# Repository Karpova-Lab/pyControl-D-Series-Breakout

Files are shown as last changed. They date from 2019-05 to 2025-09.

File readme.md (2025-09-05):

- View documentation at  https://karpova-lab.github.io/pyControl-D-Series-Breakout/
- Ask questions at https://github.com/Karpova-Lab/pyControl-D-series-Breakout/discussions
- Clone repository from https://github.com/Karpova-Lab/pyControl-D-Series-Breakout

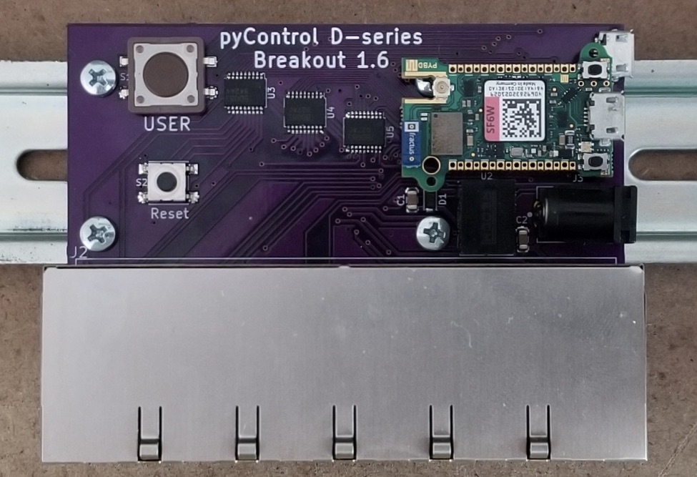
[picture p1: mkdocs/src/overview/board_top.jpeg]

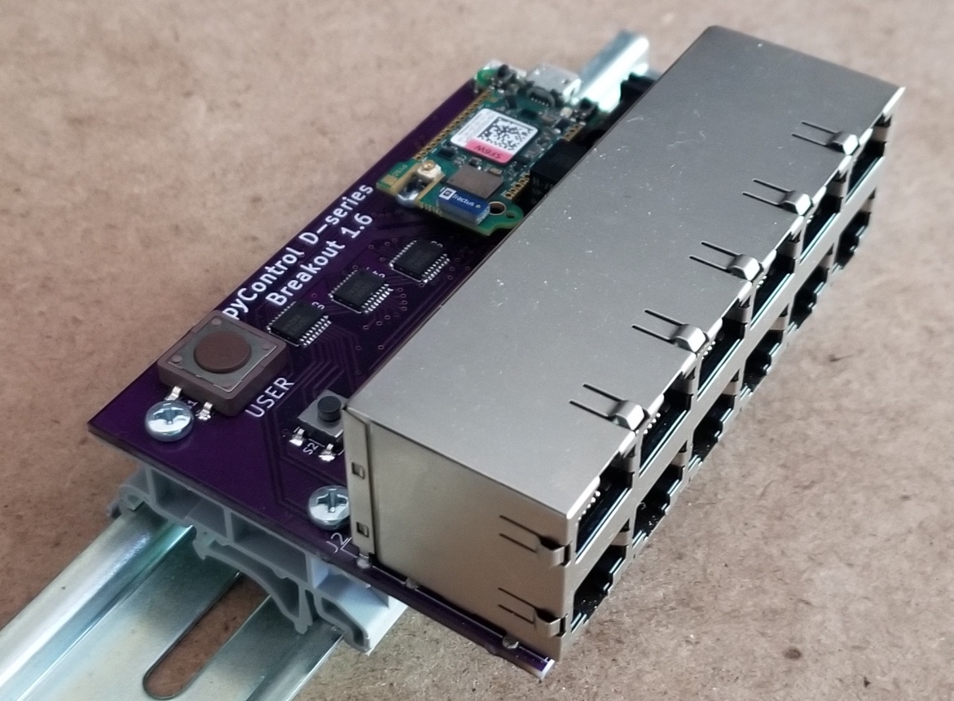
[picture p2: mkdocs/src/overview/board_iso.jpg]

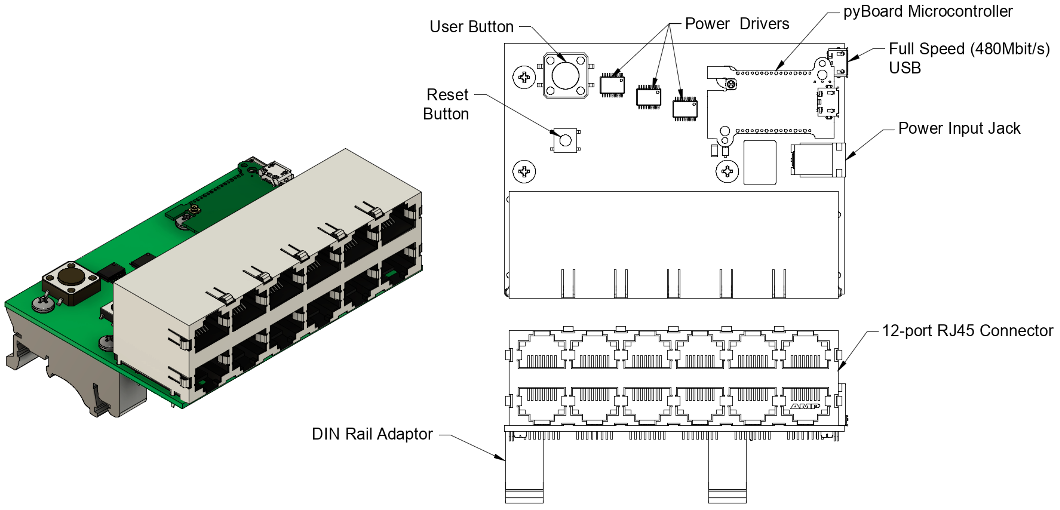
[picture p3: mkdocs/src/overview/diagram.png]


## License
This project is licensed under the [Janelia open-source hardware license](license_hardare.txt) and [Janelia 3-term BSD open-source software license](license_software.txt).

Please contact [innovation@janelia.hhmi.org](mailto:innovation@janelia.hhmi.org) if you have any questions about licensing or would like to use this project commercially.

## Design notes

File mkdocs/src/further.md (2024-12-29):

# Further Resources

## pyControl 

- [Official pyControl documentation](https://pycontrol.readthedocs.io/en/latest/) 
- [pyControl forum](https://github.com/orgs/pyControl/discussions) 
- [pyControl on GitHub](https://github.com/pyControl) 
- Purchase ready to use pyControl hardware at the [Open Ephys Store](http://www.open-ephys.org/pycontrol) or [Labmaker](https://www.labmaker.org/collections/neuroscience/products/pycontrol-mouse-behaviour-box_set_no1)

<a href="open_ephys.png">
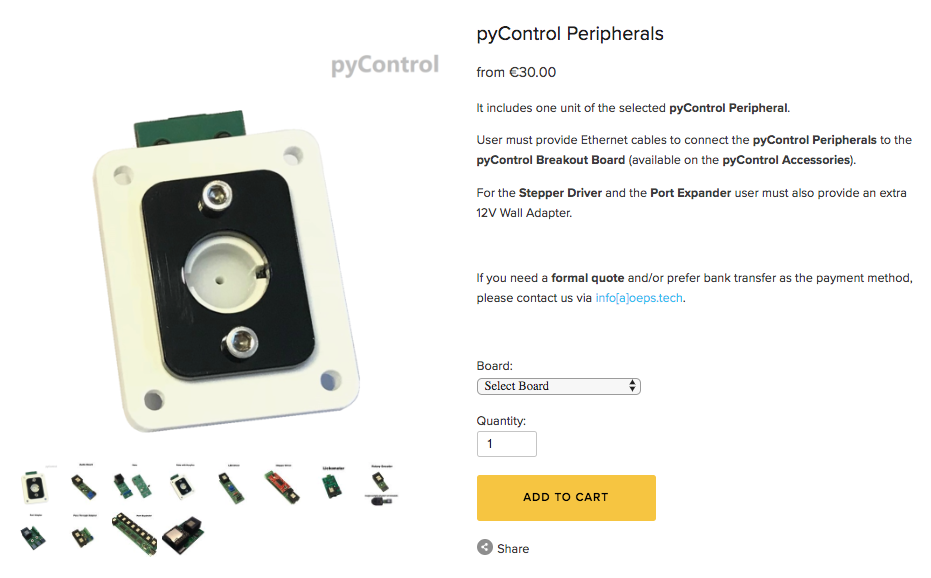
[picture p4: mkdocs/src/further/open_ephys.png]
    
</a>

## MicroPython and Pyboard D-series

- [MicroPython Documentation](http://docs.micropython.org/en/latest/) 
- [MicroPython Store](https://store.micropython.org/) 
- [Pyboard D-series Documentation](https://pybd.io/hw/pybd_sfxw.html) 

<a href="dseries.jpg">
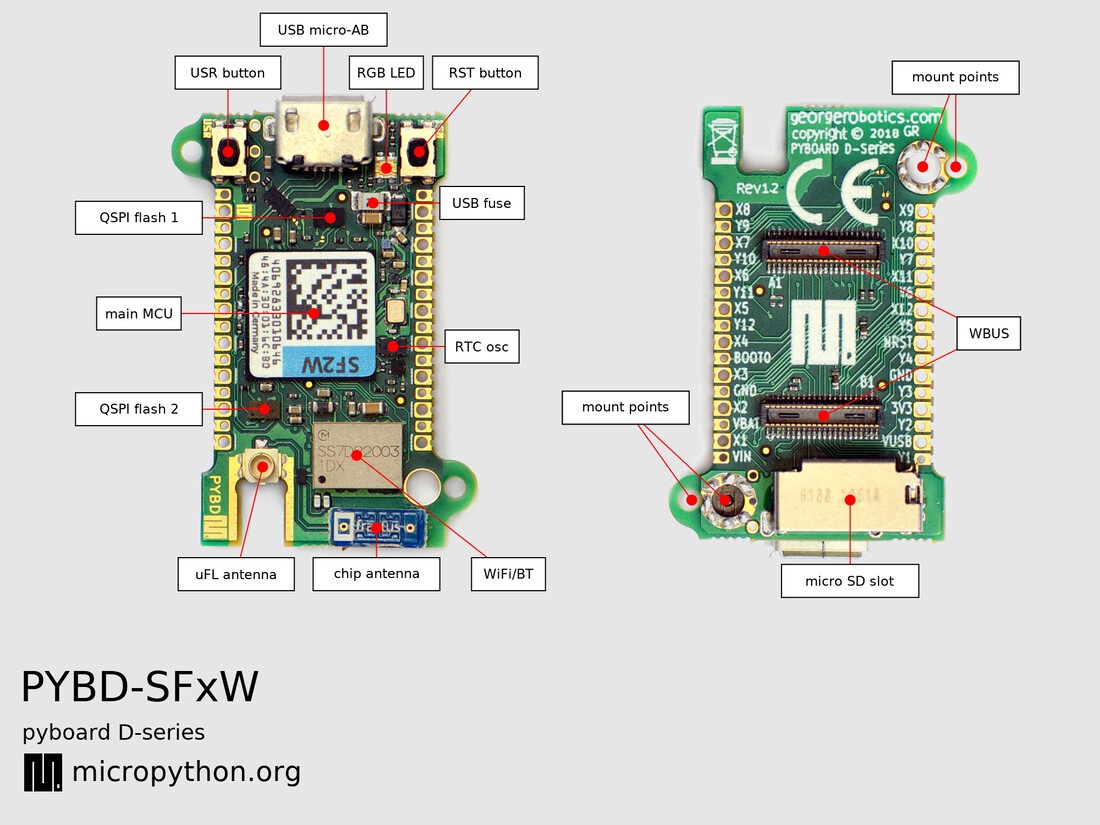
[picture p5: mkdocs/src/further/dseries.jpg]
    
</a>

## Karpova Lab
- [Lab website](https://www.janelia.org/lab/karpova-lab)
- [D-series breakout repository](https://github.com/Karpova-Lab/pyControl-D-series-Breakout)
- [More open hardware repositories](https://github.com/Karpova-Lab?type=source)
    - [Cerebro](https://karpova-lab.github.io/cerebro/)
    - [Lever](https://karpova-lab.github.io/lever/)
    - [Syringe Pump](https://karpova-lab.github.io/syringe-pump/)
    - [Nosepoke](https://karpova-lab.github.io/nosepoke/)

<a href="board_top.jpeg">
    
</a>

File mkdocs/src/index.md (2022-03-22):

# Overview

<a href="overview/board_iso.jpg">
  
</a>
<a href="overview/board_top.jpeg">
  
</a>
<a href="overview/diagram.png">
  
</a>

## What is this?

pyControl D-series breakout is a device that connects a [pyboard D-series microcontroller](https://pybd.io/hw/pybd_sfxw.html)  with twelve RJ45 ports. 
It is intended for use with the [pyControl](https://pycontrol.readthedocs.io/en/latest/) behavioral experiment control framework.

## How is it different?

<figure markdown>
  <a href="overview/side_by_side.jpeg">
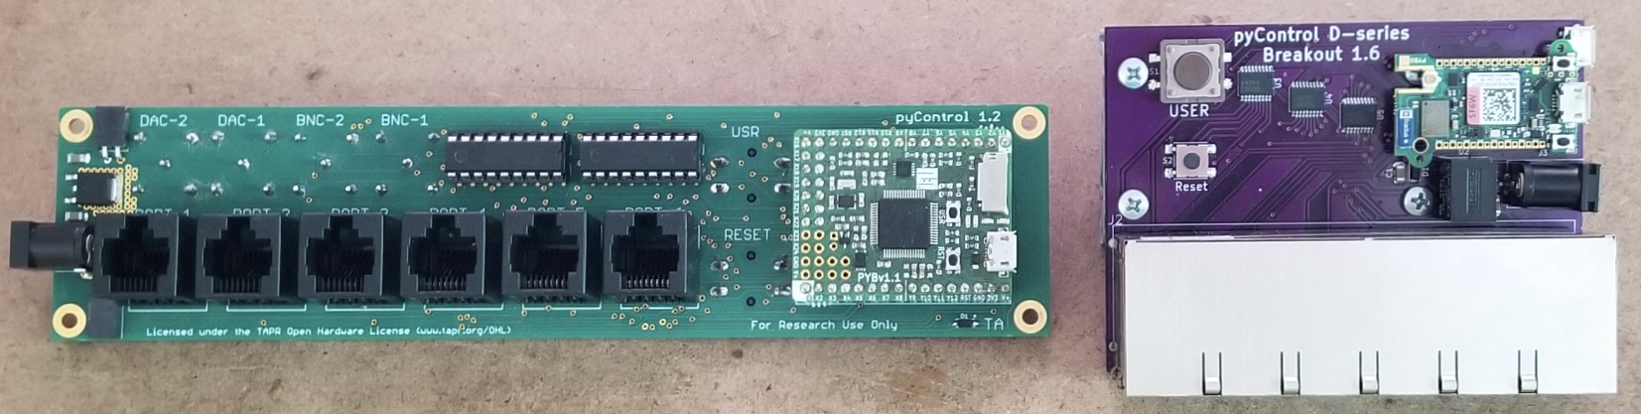
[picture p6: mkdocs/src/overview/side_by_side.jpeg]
    
  </a>
  <figcaption>pyControl Breakout Board 1.2 (left) and D-series Breakout (right)</figcaption>
</figure>

The core distinction between this breakout board and the official [pyControl breakout board 1.2](https://pycontrol.readthedocs.io/en/latest/user-guide/hardware/#breakout-board-12) is the upgrade to a newer generation pyboard (i.e. a more powerful microcontroller). 
Some benefits of the newer pyboard include being smaller, faster, having more memory, and having more input/output pins.
Having more available pins is particularly useful, as it enables the breakout board to provide more behavior ports without requiring a [port expander](https://pycontrol.readthedocs.io/en/latest/user-guide/hardware/#port-expander). 
Below is a comparison of the two breakout boards.

|                        | Breakout Board 1.2                                                | D-series Breakout Board 1.6                                                    |
|------------------------|-------------------------------------------------------------------|--------------------------------------------------------------------------------|
| **Microcontroller**    |                                                                   |                                                                                |
|    *Board*             | [pyboard v1.1](https://store.micropython.org/product/PYBv1.1#)    | [pyboard D-series SF6W](https://store.micropython.org/product/PYBD-SF6-W4F2)   |
|    *CPU*               | 168 MHz Cortex-M4F                                                | 216 MHz Cortex-M7F                                                             |
|    *RAM*               | 192 KB                                                            | 512 KB                                                                         |
|    *ROM*               | 512 KB                                                            | 4,048 KB                                                                       |
| **Connectors**         |                                                                   |                                                                                |
|    *RJ45*              | 6                                                                 | 12                                                                             |
|    *BNC*               | 4                                                                 | 0                                                                              |
|    *USB*               | Full Speed (12 Mbit/s)                                            | High Speed (480 Mbit/s)                                                        |
| **Behavior Ports**     |                                                                   |                                                                                |
|    *Power Driver Pins* | 14                                                                | 24                                                                             |
|    *Digital I/O Pins*  | 14                                                                | 30                                                                             |
|    *ADC Pins*          | 12                                                                | 15                                                                             |
|    *DAC Pins*          | 2                                                                 | 2                                                                              |
|    *UART Buses*        | 3                                                                 | 4                                                                              |
|    *I2C Buses*         | 2                                                                 | 2                                                                              |
| **Dimensions**         |                                                                   |                                                                                |
|    *PCB*               | 1.8 in x 7.6 in                                                   | 2.7 in x 3.6 in                                                                |
| **Performance**[^1]    |                                                                   |                                                                                |
| *Latency - No load*    | 561 ± 16 µs (100% < 1 ms)                                         | 307 ± 9 µs (100% < 1 ms)                                                       |
| *Latency - High load*  | 842 ± 293 µs (84.8% < 1 ms)                                       | 372 ± 95 µs (100% < 1 ms)                                                      |
| *Accuracy - No load*   | -210 ± 281 µs (100% < 1 ms)                                       | -342 ± 285 µs (100% < 1 ms)                                                    |
| *Accuracy - High load* | -27 ± 351 µs (99.2% < 1 ms)                                       | -361 ± 280 µs (100% < 1 ms)                                                    |

<a href="overview/timing_comparison.png">
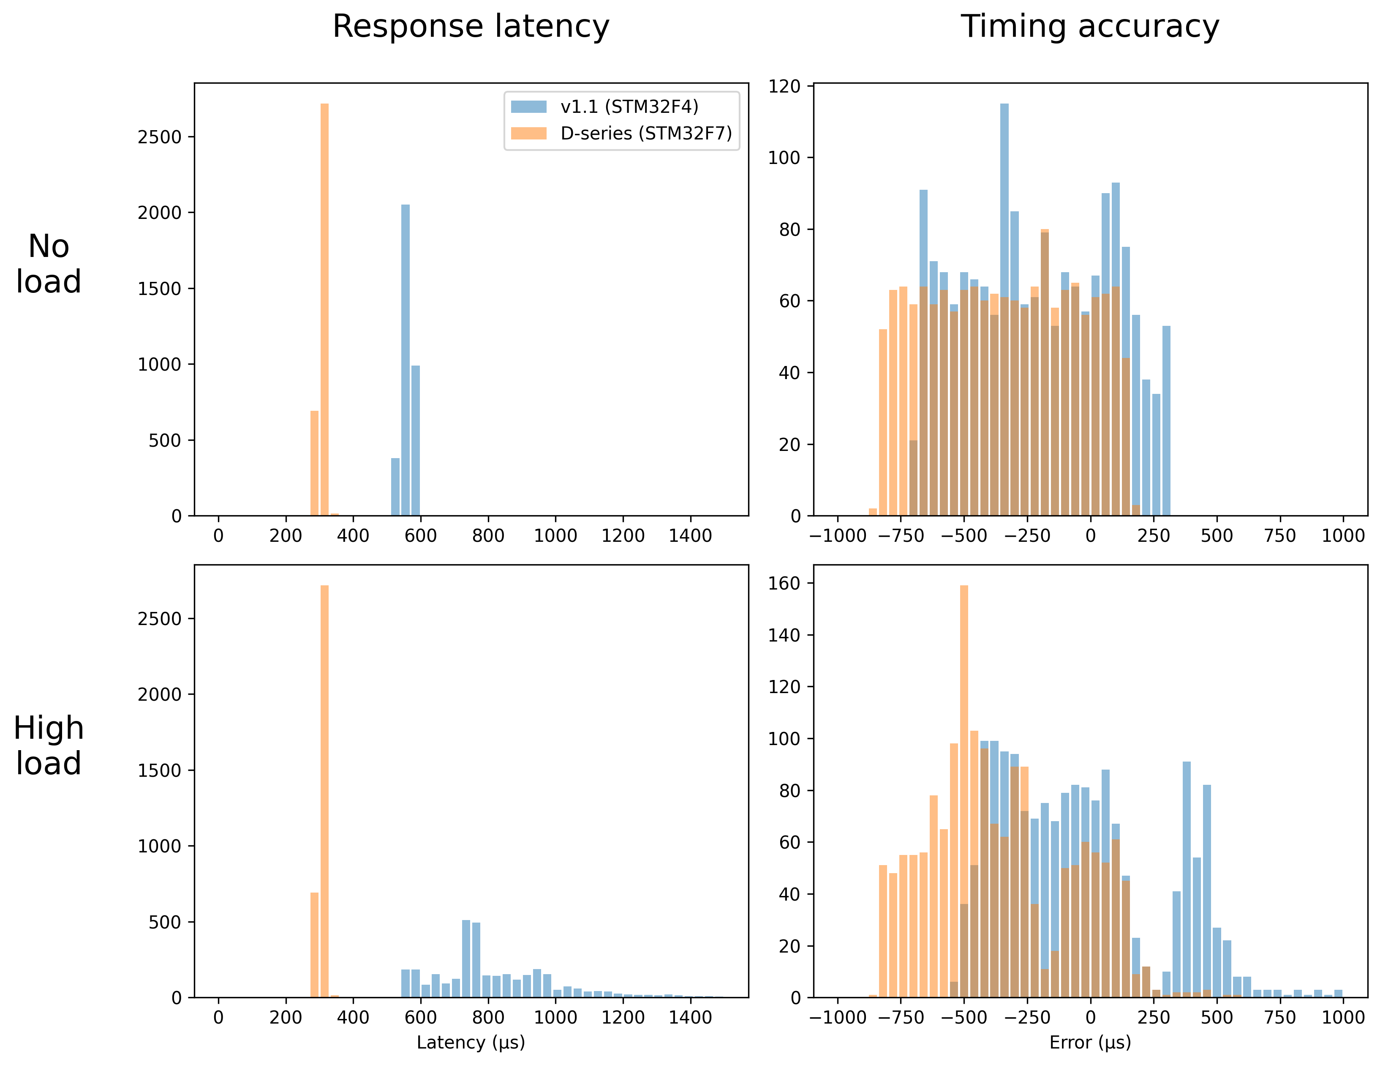
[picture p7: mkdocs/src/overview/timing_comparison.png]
  
</a>

[^1]: More details about the performance comparison [here](https://github.com/Karpova-Lab/pyControl-D-Series-Breakout/tree/master/benchmarking).

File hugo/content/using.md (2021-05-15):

# Using

## What To Get

| Qty | Description                    | Order Link                                                           | Required |
|---|----------------------------------|----------------------------------------------------------------------|----------|
| 1 | D-series Breakout Board          | [Build your own]({{< ref "building" >}})                             | Yes      |
| 1 | pyboard D-series Microcontroller | [Micropython](https://store.micropython.org/product/PYBD-SF6-W4F2)   | Yes      |
| 1 | 12V DC Power Supply              | [Digi-Key](https://www.digikey.com/products/en?keywords=102-3631-ND) | Yes      |
| 1 | USB cable                        | [Digi-Key](https://www.digikey.com/products/en?keywords=380-1431-ND) | Yes      |
| 1 | DIN Rail                         | [Digi-Key](https://www.digikey.com/short/prn3bb)                     |          |
| 2 | DIN Rail Adapter                 | [Digi-Key](https://www.digikey.com/products/en?keywords=277-2296-nd) |          |
| 4 | M3 screws                        | [Digi-Key](https://www.digikey.com/products/en?keywords=335-1156-ND) |          |

## First Time Setup

{{< hint warning >}}
### <i class="fas fa-exclamation-triangle"></i> **Attention** 

The breakout board is designed to use the microcontroller's high speed USB interface. We must make a change to ``boot.py`` so that everything works properly https://pybd.io/hw/pybd_sfxw.html#usb-ports.

1. Plug the bare pyBoard D-series into your computer. 

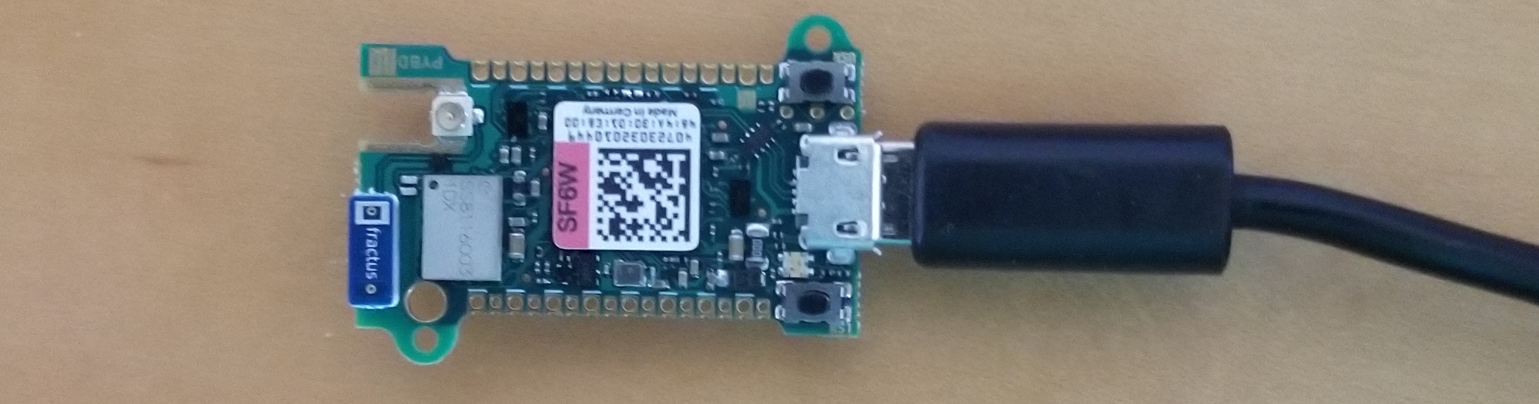
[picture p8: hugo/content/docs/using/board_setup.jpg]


2. It should appear as a flash drive on your computer. Edit the ``boot.py`` file to have the following:

```python
import pyb
pyb.usb_mode('VCP',port=1)
```

This change to ``boot.py`` is required, otherwise the pyboard won't be found by the pyControl software when it is connected through the breakout board! 

{{< /hint >}}

You are now ready to connect to the D-series Breakout board.

1. Plug the pyBoard onto the breakout board
2. Plug 12V DC power into the breakout board
3. Connect the breakout board to your computer with the USB

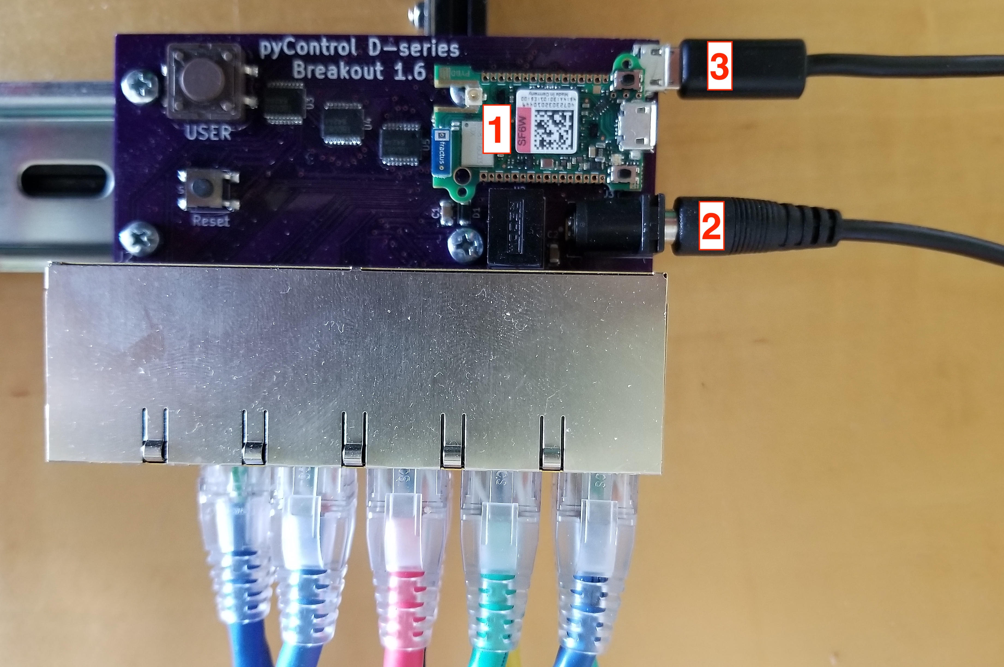
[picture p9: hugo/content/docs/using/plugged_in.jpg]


## Connecting Peripheral Devices
Refer to the table below when considering where to plug in devices. Fill up the top row first with standard devices that just need inputs or outputs. Use the second row for devices that require special communication (UART or I<sup>2</sup>C).

{{< hint info >}}
### <i class="fas fa-info-circle"></i> Note
The pyBoard microcontroller is limited to 16 seperate interrupt vectors (https://forum.micropython.org/viewtopic.php?t=2271). 
All of the DIO pins on the top row of the breakout board (Ports 1-6) are on separate interrupt vectors, so if you have a lot of input devices, plug them into the top row where there is a guarantee of no interrupt vector collisions.
{{< /hint >}}

{{< hint info >}}
### <i class="fas fa-info-circle"></i> Note
If you need to connect to a peripheral using SPI, take a look at Micropython's [machine.SoftSPI](https://docs.micropython.org/en/latest/library/machine.SPI.html)

The hardware SPI pins are unfortunately not grouped together on a single RJ45 jack on this breakout board, but instead are split up among multiple ports. 
If you absolutely need to access the hardware SPI pins, you can plug in multiple [port adapters](https://open-ephys.org/pycontrol/pycontrol-peripherals) to expose the pins. 
Information on which hardware SPI pins are where can be found in <a href="spi_ports.xlsx" download > <i class="fa fa-download"></i>this spreadsheet </a>
{{< /hint >}}

<a href="pinouts.jpg">
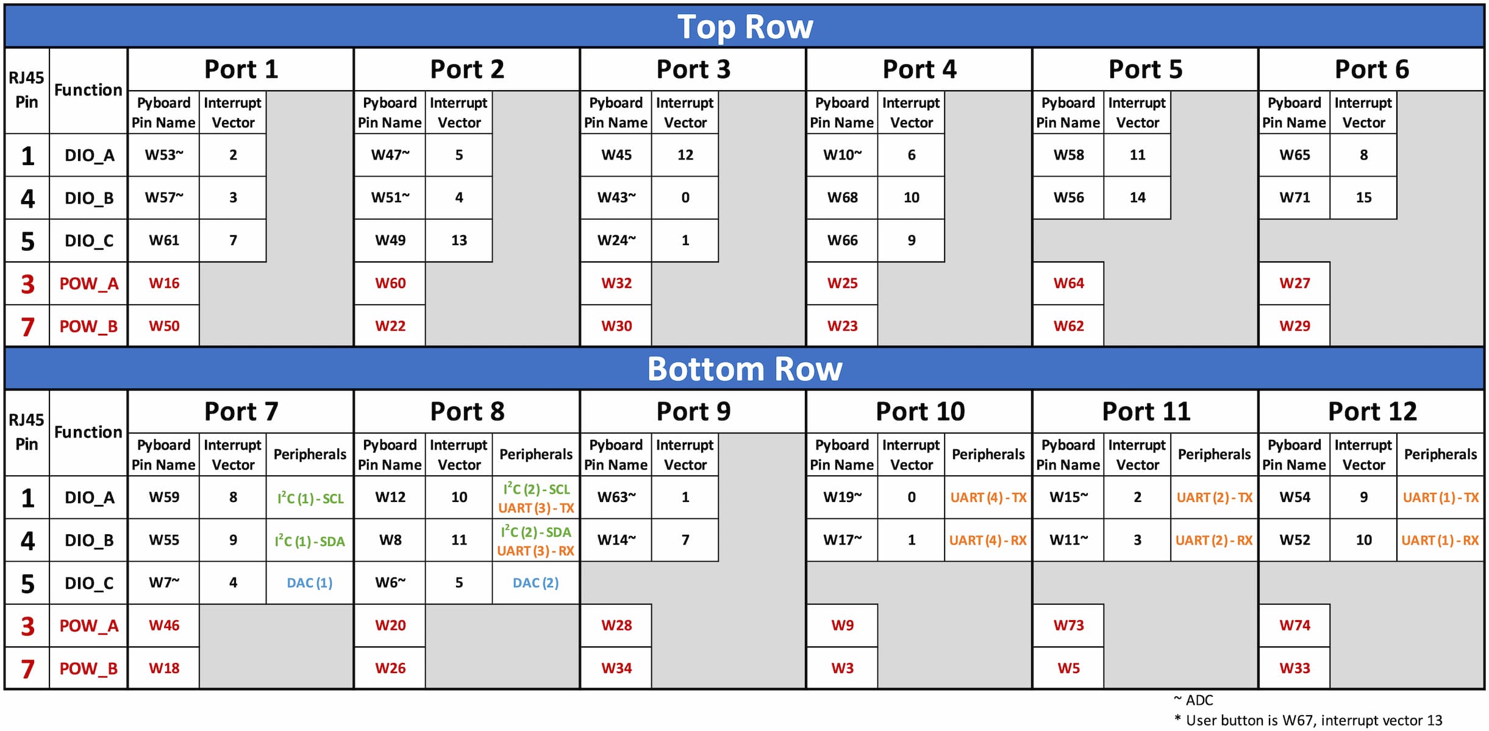
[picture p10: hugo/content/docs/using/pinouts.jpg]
  
</a>
<br>
{{< caption text="Mapping of pins to ports (click to enlarge)" >}}

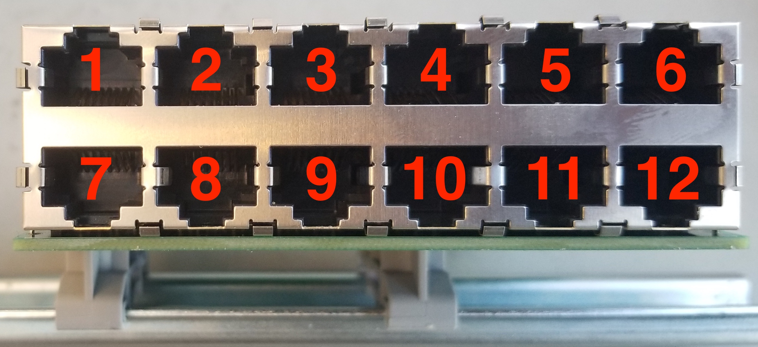
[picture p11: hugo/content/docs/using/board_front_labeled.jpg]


## Example Task
The following instructions will enable you to run the ``hardware_test.py`` task file that comes with pyControl. The task uses 3 nosepokes plugged into ports 1-3 and a houselight plugged into port 4.

1. Download the latest version of [pyControl](https://github.com/pyControl/code/releases)
2. Download {{< download filename="breakout_dseries_1_6.py" text="breakout_dseries_1_6.py">}} and place it in the ``devices\`` directory
3. Download {{< download filename="new_hardware_definition.py" text="new_hardware_definition.py">}} and place it in the ``config\`` directory

```
.
└─ pyControl
   ├ config
   │  └─ new_hardware_definition.py
   └─ devices
      └─ breakout_dseries_1_6.py
```

<!-- .. #pyControl
.. ##config
.. ###new_hardware_definition_1_6.py
.. ##devices
.. ###_breakout_dseries.py -->

4. Launch pyControl and press the "Connect" button to connect to the breakout board.
5. Press the "Config" button and the "Load framework" button. 
6. Again, press the "Config" button. Press the "Load hardware definition" button and then select "new_hardware_definition.py" to upload.
7. If succesfull, you should get a couple OK's

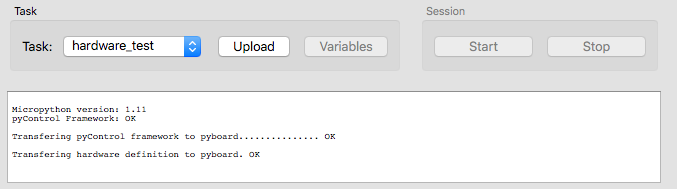
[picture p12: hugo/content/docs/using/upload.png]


8. From the task dropdown, select "examples/hardware_test", then click "Upload".
9. Click "Start". The houselight should turn on and nosepokes will now respond to pokes.

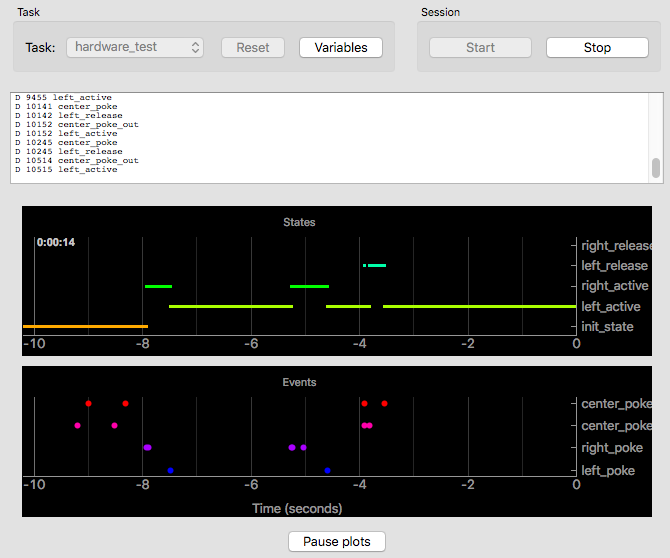
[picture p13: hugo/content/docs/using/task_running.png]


{{< previous link="building" text="Building" >}}
{{< next link="further" text="Further Resources" >}}

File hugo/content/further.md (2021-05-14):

# Further Resources
-----------------

## pyControl 

{{< columns >}}

- [Official pyControl documentation](https://pycontrol.readthedocs.io/en/latest/) 
- [pyControl Google groups forum](https://groups.google.com/forum/#!forum/pycontrol) 
- [pyControl software repository](https://github.com/pyControl/pyControl) 
    - [Download Page](https://github.com/pyControl/pyControl/releases)
- [pyControl hardware repository](https://github.com/ThomasAkam/pyControl_hardware) 
- Purchase ready to use pyControl hardware at the [Open Ephys Store](http://www.open-ephys.org/pycontrol) 

<--->



{{< /columns >}}

## MicroPython and Pyboard D-series

{{< columns >}}

- [MicroPython Documentation](http://docs.micropython.org/en/latest/) 
- [MicroPython Store](https://store.micropython.org/) 
- [Pyboard D-series Documentation](https://pybd.io/hw/pybd_sfxw.html) 

<--->



{{< /columns >}}

## Karpova Lab
{{< columns >}}

- [Lab website](https://www.janelia.org/lab/karpova-lab)
- [D-series breakout repository](https://github.com/Karpova-Lab/pyControl-D-series-Breakout)
- [More open hardware repositories](https://github.com/Karpova-Lab?type=source)
    - [Cerebro](https://karpova-lab.github.io/cerebro/)
    - [Lever](https://karpova-lab.github.io/Lever/)
    - [Syringe Pump](https://karpova-lab.github.io/syringe-pump/)
    - [Nosepoke](https://karpova-lab.github.io/nosepoke/)

<--->

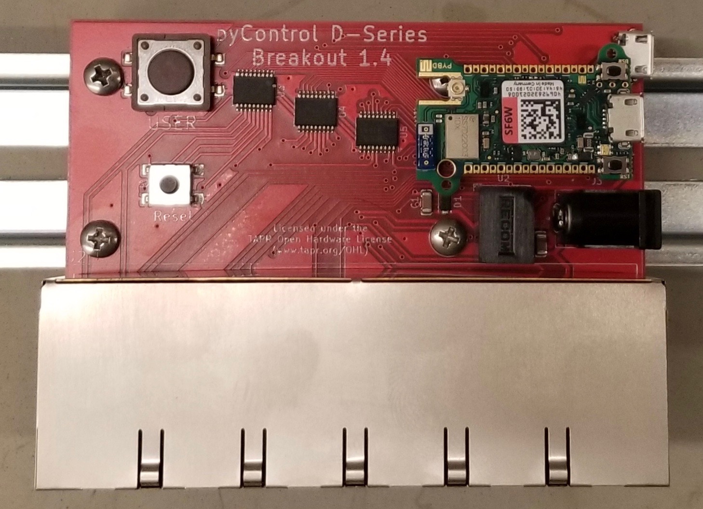
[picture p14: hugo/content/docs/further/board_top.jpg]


{{< /columns >}}

{{< previous link="using" text="Using" >}}

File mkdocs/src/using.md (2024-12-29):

# Using

## What To Get

| Qty | Description                    | Order Link                                                           | Required |
|---|----------------------------------|----------------------------------------------------------------------|----------|
| 1 | D-series Breakout Board          | [Build your own](building.md#printed-circuit-board)    | Yes      |
| 1 | pyboard D-series Microcontroller | [Micropython](https://store.micropython.org/category/pyboard%20D-series)   | Yes      |
| 1 | 12V DC Power Supply              | [Digi-Key](https://www.digikey.com/products/en?keywords=102-3631-ND) | Yes      |
| 1 | USB cable                        | [Digi-Key](https://www.digikey.com/products/en?keywords=380-1431-ND) | Yes      |
| 1 | DIN Rail                         | [Digi-Key](https://www.digikey.com/short/q8mq0f3n)                   |          |
| 2 | DIN Rail Adapter                 | [Digi-Key](https://www.digikey.com/products/en?keywords=277-2296-nd) |          |
| 4 | M3 screws                        | [Digi-Key](https://www.digikey.com/products/en?keywords=335-1156-ND) |          |

## First Time Setup

!!! warning "Important HS USB setup"

    The breakout board is designed to use the [pyboard's high speed USB interface](https://pybd.io/hw/pybd_sfxw.html#usb-ports). To ensure the correct usb mode is being used, we make a change to the ``boot.py`` file.

    1. Plug the bare pyboard D-series into your computer. 
    
    2. It should appear as a flash drive on your computer. Edit the ``boot.py`` file to have the following:
    ```python
    import pyb
    pyb.usb_mode('VCP',port=1)
    ```

    This change to ``boot.py`` is required, otherwise the pyboard won't be found by the pyControl software when it is connected through the breakout board! 

You are now ready to connect to the D-series Breakout board.

1. Plug the pyboard onto the breakout board
2. Plug 12V DC power into the breakout board
3. Connect the breakout board to your computer with the USB


## Connecting Peripheral Devices
Refer to the table below when considering where to plug in devices. Fill up the top row first with standard devices that just need inputs or outputs. Use the second row for devices that require special communication (UART or I<sup>2</sup>C).

???+ note "Note on interrupts"
    The pyboard microcontroller is limited to [16 separate interrupt vectors](https://forum.micropython.org/viewtopic.php?t=2271). 
    All of the DIO pins on the top row of the breakout board (Ports 1-6) are on separate interrupt vectors, so if you have a lot of input devices, plug them into the top row where there is a guarantee of no interrupt vector collisions.

???+ note "Note on SPI"
    If you need to connect to a peripheral using SPI, take a look at Micropython's [machine.SoftSPI](https://docs.micropython.org/en/latest/library/machine.SPI.html)

    The hardware SPI pins are unfortunately not grouped together on a single RJ45 jack on this breakout board, but instead are split up among multiple ports. 
    If you absolutely need to access the hardware SPI pins, you can plug in multiple [port adapters](https://open-ephys.org/pycontrol/pycontrol-peripherals) to expose the pins. 

    The following table desribes  hardware SPI pin mapping.

    <table style="border-collapse:collapse;border-spacing:0" class="tg"><thead><tr><th style="border-color:inherit;border-style:solid;border-width:1px;font-family:Arial, sans-serif;font-size:14px;font-weight:normal;overflow:hidden;padding:10px 5px;text-align:left;vertical-align:top;word-break:normal"> </th><th style="border-color:inherit;border-style:solid;border-width:1px;font-family:Arial, sans-serif;font-size:14px;font-weight:normal;overflow:hidden;padding:10px 5px;text-align:left;vertical-align:top;word-break:normal">SPI function</th><th style="border-color:inherit;border-style:solid;border-width:1px;font-family:Arial, sans-serif;font-size:14px;font-weight:normal;overflow:hidden;padding:10px 5px;text-align:left;vertical-align:top;word-break:normal">CPU name</th><th style="border-color:inherit;border-style:solid;border-width:1px;font-family:Arial, sans-serif;font-size:14px;font-weight:normal;overflow:hidden;padding:10px 5px;text-align:left;vertical-align:top;word-break:normal">Pin name</th><th style="border-color:inherit;border-style:solid;border-width:1px;font-family:Arial, sans-serif;font-size:14px;font-weight:normal;overflow:hidden;padding:10px 5px;text-align:left;vertical-align:top;word-break:normal">other pin name</th><th style="border-color:inherit;border-style:solid;border-width:1px;font-family:Arial, sans-serif;font-size:14px;font-weight:normal;overflow:hidden;padding:10px 5px;text-align:left;vertical-align:top;word-break:normal">D-series breakout  port</th><th style="border-color:inherit;border-style:solid;border-width:1px;font-family:Arial, sans-serif;font-size:14px;font-weight:normal;overflow:hidden;padding:10px 5px;text-align:left;vertical-align:top;word-break:normal">port function</th></tr></thead><tbody><tr><td style="border-color:inherit;border-style:solid;border-width:1px;font-family:Arial, sans-serif;font-size:14px;overflow:hidden;padding:10px 5px;text-align:left;vertical-align:top;word-break:normal" rowspan="3">SPI(1)</td><td style="border-color:inherit;border-style:solid;border-width:1px;font-family:Arial, sans-serif;font-size:14px;overflow:hidden;padding:10px 5px;text-align:center;vertical-align:top;word-break:normal">SCK</td><td style="border-color:inherit;border-style:solid;border-width:1px;font-family:Arial, sans-serif;font-size:14px;overflow:hidden;padding:10px 5px;text-align:center;vertical-align:top;word-break:normal">A5</td><td style="border-color:inherit;border-style:solid;border-width:1px;font-family:Arial, sans-serif;font-size:14px;overflow:hidden;padding:10px 5px;text-align:center;vertical-align:top;word-break:normal">x6</td><td style="border-color:inherit;border-style:solid;border-width:1px;font-family:Arial, sans-serif;font-size:14px;overflow:hidden;padding:10px 5px;text-align:center;vertical-align:top;word-break:normal">W6</td><td style="border-color:inherit;border-style:solid;border-width:1px;font-family:Arial, sans-serif;font-size:14px;overflow:hidden;padding:10px 5px;text-align:center;vertical-align:top;word-break:normal">8</td><td style="border-color:inherit;border-style:solid;border-width:1px;font-family:Arial, sans-serif;font-size:14px;overflow:hidden;padding:10px 5px;text-align:center;vertical-align:top;word-break:normal">C</td></tr><tr><td style="border-color:inherit;border-style:solid;border-width:1px;font-family:Arial, sans-serif;font-size:14px;overflow:hidden;padding:10px 5px;text-align:center;vertical-align:top;word-break:normal">MISO</td><td style="border-color:inherit;border-style:solid;border-width:1px;font-family:Arial, sans-serif;font-size:14px;overflow:hidden;padding:10px 5px;text-align:center;vertical-align:top;word-break:normal">A6</td><td style="border-color:inherit;border-style:solid;border-width:1px;font-family:Arial, sans-serif;font-size:14px;overflow:hidden;padding:10px 5px;text-align:center;vertical-align:top;word-break:normal">x7</td><td style="border-color:inherit;border-style:solid;border-width:1px;font-family:Arial, sans-serif;font-size:14px;overflow:hidden;padding:10px 5px;text-align:center;vertical-align:top;word-break:normal">W10</td><td style="border-color:inherit;border-style:solid;border-width:1px;font-family:Arial, sans-serif;font-size:14px;overflow:hidden;padding:10px 5px;text-align:center;vertical-align:top;word-break:normal">4</td><td style="border-color:inherit;border-style:solid;border-width:1px;font-family:Arial, sans-serif;font-size:14px;overflow:hidden;padding:10px 5px;text-align:center;vertical-align:top;word-break:normal">A</td></tr><tr><td style="border-color:inherit;border-style:solid;border-width:1px;font-family:Arial, sans-serif;font-size:14px;overflow:hidden;padding:10px 5px;text-align:center;vertical-align:top;word-break:normal">MOSI</td><td style="border-color:inherit;border-style:solid;border-width:1px;font-family:Arial, sans-serif;font-size:14px;overflow:hidden;padding:10px 5px;text-align:center;vertical-align:top;word-break:normal">A7</td><td style="border-color:inherit;border-style:solid;border-width:1px;font-family:Arial, sans-serif;font-size:14px;overflow:hidden;padding:10px 5px;text-align:center;vertical-align:top;word-break:normal">x8</td><td style="border-color:inherit;border-style:solid;border-width:1px;font-family:Arial, sans-serif;font-size:14px;overflow:hidden;padding:10px 5px;text-align:center;vertical-align:top;word-break:normal">W14</td><td style="border-color:inherit;border-style:solid;border-width:1px;font-family:Arial, sans-serif;font-size:14px;overflow:hidden;padding:10px 5px;text-align:center;vertical-align:top;word-break:normal">9</td><td style="border-color:inherit;border-style:solid;border-width:1px;font-family:Arial, sans-serif;font-size:14px;overflow:hidden;padding:10px 5px;text-align:center;vertical-align:top;word-break:normal">B</td></tr><tr><td style="border-color:inherit;border-style:solid;border-width:1px;font-family:Arial, sans-serif;font-size:14px;overflow:hidden;padding:10px 5px;text-align:left;vertical-align:top;word-break:normal" rowspan="3">SPI(2)</td><td style="border-color:inherit;border-style:solid;border-width:1px;font-family:Arial, sans-serif;font-size:14px;overflow:hidden;padding:10px 5px;text-align:center;vertical-align:top;word-break:normal">SCK</td><td style="border-color:inherit;border-style:solid;border-width:1px;font-family:Arial, sans-serif;font-size:14px;overflow:hidden;padding:10px 5px;text-align:center;vertical-align:top;word-break:normal">B13</td><td style="border-color:inherit;border-style:solid;border-width:1px;font-family:Arial, sans-serif;font-size:14px;overflow:hidden;padding:10px 5px;text-align:center;vertical-align:top;word-break:normal">y6</td><td style="border-color:inherit;border-style:solid;border-width:1px;font-family:Arial, sans-serif;font-size:14px;overflow:hidden;padding:10px 5px;text-align:center;vertical-align:top;word-break:normal">W49</td><td style="border-color:inherit;border-style:solid;border-width:1px;font-family:Arial, sans-serif;font-size:14px;overflow:hidden;padding:10px 5px;text-align:center;vertical-align:top;word-break:normal">2</td><td style="border-color:inherit;border-style:solid;border-width:1px;font-family:Arial, sans-serif;font-size:14px;overflow:hidden;padding:10px 5px;text-align:center;vertical-align:top;word-break:normal">C</td></tr><tr><td style="border-color:inherit;border-style:solid;border-width:1px;font-family:Arial, sans-serif;font-size:14px;overflow:hidden;padding:10px 5px;text-align:center;vertical-align:top;word-break:normal">MISO</td><td style="border-color:inherit;border-style:solid;border-width:1px;font-family:Arial, sans-serif;font-size:14px;overflow:hidden;padding:10px 5px;text-align:center;vertical-align:top;word-break:normal">C2</td><td style="border-color:inherit;border-style:solid;border-width:1px;font-family:Arial, sans-serif;font-size:14px;overflow:hidden;padding:10px 5px;text-align:center;vertical-align:top;word-break:normal">y7</td><td style="border-color:inherit;border-style:solid;border-width:1px;font-family:Arial, sans-serif;font-size:14px;overflow:hidden;padding:10px 5px;text-align:center;vertical-align:top;word-break:normal">W53</td><td style="border-color:inherit;border-style:solid;border-width:1px;font-family:Arial, sans-serif;font-size:14px;overflow:hidden;padding:10px 5px;text-align:center;vertical-align:top;word-break:normal">1</td><td style="border-color:inherit;border-style:solid;border-width:1px;font-family:Arial, sans-serif;font-size:14px;overflow:hidden;padding:10px 5px;text-align:center;vertical-align:top;word-break:normal">A</td></tr><tr><td style="border-color:inherit;border-style:solid;border-width:1px;font-family:Arial, sans-serif;font-size:14px;overflow:hidden;padding:10px 5px;text-align:center;vertical-align:top;word-break:normal">MOSI</td><td style="border-color:inherit;border-style:solid;border-width:1px;font-family:Arial, sans-serif;font-size:14px;overflow:hidden;padding:10px 5px;text-align:center;vertical-align:top;word-break:normal">C3</td><td style="border-color:inherit;border-style:solid;border-width:1px;font-family:Arial, sans-serif;font-size:14px;overflow:hidden;padding:10px 5px;text-align:center;vertical-align:top;word-break:normal">y8</td><td style="border-color:inherit;border-style:solid;border-width:1px;font-family:Arial, sans-serif;font-size:14px;overflow:hidden;padding:10px 5px;text-align:center;vertical-align:top;word-break:normal">W57</td><td style="border-color:inherit;border-style:solid;border-width:1px;font-family:Arial, sans-serif;font-size:14px;overflow:hidden;padding:10px 5px;text-align:center;vertical-align:top;word-break:normal">1</td><td style="border-color:inherit;border-style:solid;border-width:1px;font-family:Arial, sans-serif;font-size:14px;overflow:hidden;padding:10px 5px;text-align:center;vertical-align:top;word-break:normal">B</td></tr></tbody></table>
    [https://store.micropython.org/media/products/PYBD_SF2_W4F2_ds2.jpg](https://store.micropython.org/media/products/PYBD_SF2_W4F2_ds2.jpg)
    [https://store.micropython.org/media/products/WBUS_DIP68_ds1.jpg](https://store.micropython.org/media/products/WBUS_DIP68_ds1.jpg)

<a href="pinouts.jpg">
    
</a>
<a href="board_front_labeled.jpg">
    
</a>

## Example Task
The following instructions will enable you to run the ``hardware_test.py`` task file that comes with pyControl. The task uses 3 nosepokes plugged into ports 1-3 and a houselight plugged into port 4.

1. Download the latest version of [pyControl](https://github.com/pyControl/code/releases)
2. Download <a href="breakout_dseries_1_6.py" download >:material-file-download: breakout_dseries_1_6.py</a> and place it in the ``devices\`` directory
3. Download <a href="new_hardware_definition.py" download >:material-file-download: new_hardware_definition.py</a> and place it in the ``config\`` directory 
```
.
└─ pyControl
   ├ config
   │  └─ new_hardware_definition.py
   └─ devices
      └─ breakout_dseries_1_6.py
```
4. Launch pyControl and press the "Connect" button to connect to the breakout board.
5. Press the "Config" button and the "Load framework" button. 
6. Again, press the "Config" button. Press the "Load hardware definition" button and then select "new_hardware_definition.py" to upload.
7. If successful, you should get a couple OK's confirming that the framework and hardware definition have been transferred.

8. From the task dropdown, select "examples/hardware_test", then click "Upload".
9. Click "Start". The houselight should turn on and nosepokes will now respond to pokes.


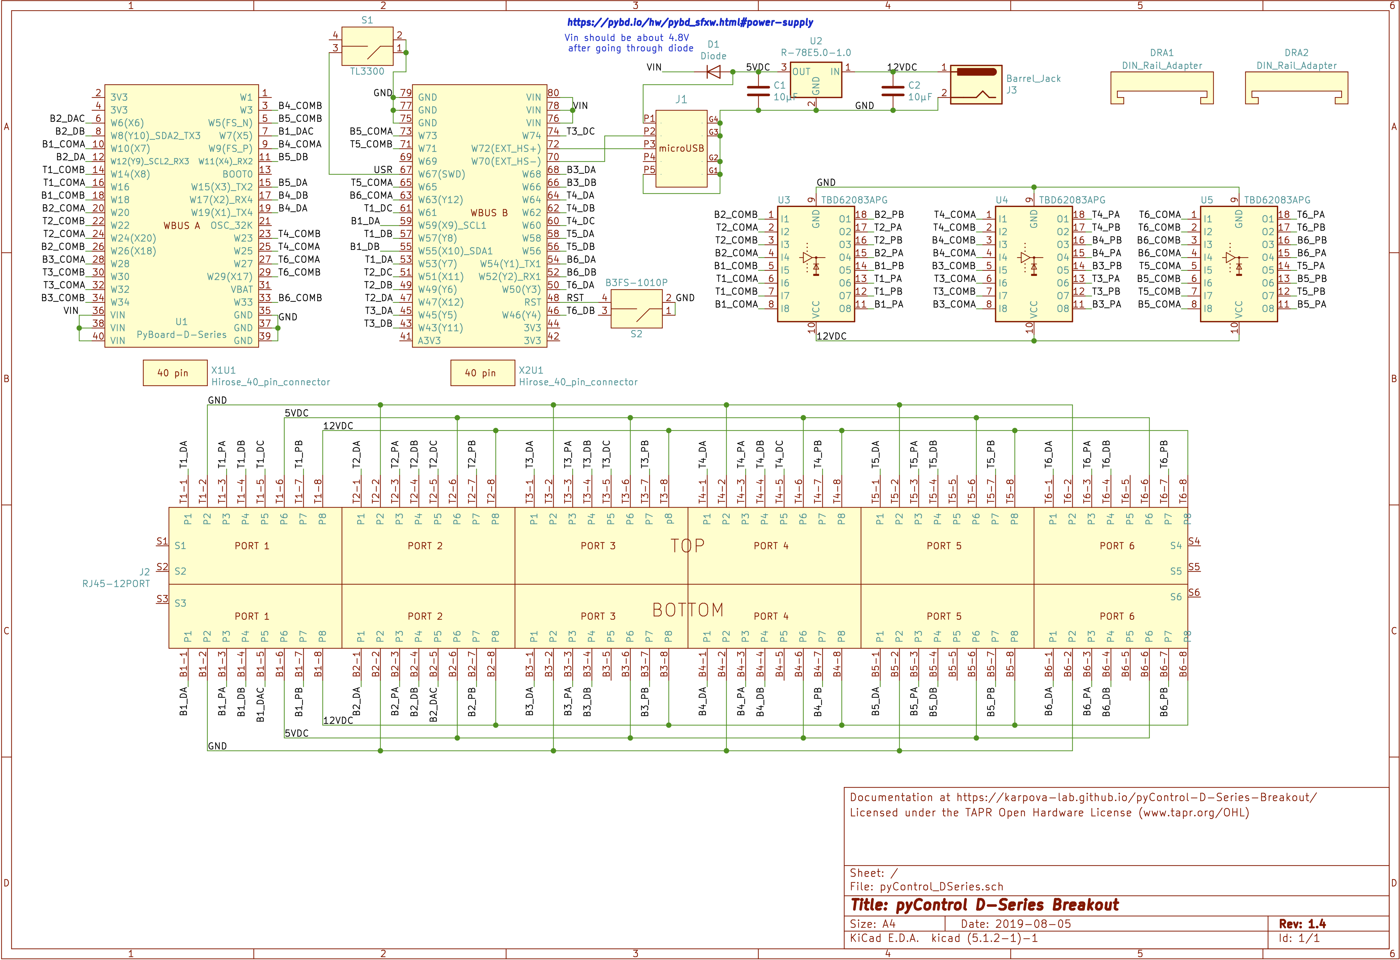
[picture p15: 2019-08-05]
docs/_images/schematic.png

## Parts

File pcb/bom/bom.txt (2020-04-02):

"Qty","Reference","Description","Value/MPN","Purchase Link"
"2","C2, C1","1206 Capacitor","10µF","https://www.digikey.com/products/en?keywords=1276-1804-1-ND"
"1","D1","Schottky Diode","MBR120VLSFT3G","https://www.digikey.com/products/en?keywords=MBR120VLSFT3GOSCT-ND"
"1","J1","Micro USB Socket","10118194-0001LF","https://www.digikey.com/products/en?keywords=609-4618-1-ND"
"1","J2","12-port RJ45 Connector","5569263-1","https://www.digikey.com/products/en?keywords=5569263"
"1","J3","Barrel Jack Connector","PJ-037A","https://www.digikey.com/product-detail/en/cui-inc/PJ-037A/CP-037A-ND/1644545"
"1","S1","Large Tactile Switch","TL3300DF160Q","https://www.digikey.com/products/en?keywords=EG4906CT-ND"
"1","S2","Small Tactile Switch","B3FS-1010P","https://www.digikey.com/products/en?keywords=sw1440ct"
"1","U2","5V DC to DC Converter","R-78E5.0-1.0","https://www.digikey.com/products/en?keywords=945-2201-ND"
"3","U5, U4, U3","8-channel Driver Array","TBD62083A","https://www.digikey.com/products/en?keywords=TBD62083AFNGELCT-ND"
"2","X2U1, X1U1","40-pin Connector","DF40HC(4.0)-40DS-0.4V(70)","https://www.digikey.com/products/en?keywords=H124604CT-ND"

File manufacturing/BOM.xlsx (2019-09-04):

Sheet: pyboardbreakout
Qty | Description | Datasheet | Order Link
1 | Printed Circuit Board | :download:`pyControl D-Series Breakout 1.4<../../manufacturing/datasheets/breakout.pdf>` | `OSH Park <https://oshpark.com/shared_projects/qB3NMaHN>`_
1 | Large Button | :download:`TL3300DF160Q<../../manufacturing/datasheets/tactile_switch_large.pdf>` | `Digi-Key <https://www.digikey.com/products/en?keywords=EG4906CT-ND>`_
1 | Small Button | :download:`B3FS-1010P<../../manufacturing/datasheets/tactile_switch_small.pdf>` | `Digi-Key <https://www.digikey.com/products/en?keywords=sw1440ct>`_
1 | Barrel Jack Connector | :download:`PJ-037A<../../manufacturing/datasheets/barrel_jack.pdf>` | `Digi-Key <https://www.digikey.com/products/en?keywords=CP-037A-ND>`_
2 | 12-Port RJ45 Connector | :download:`5569263-1<../../manufacturing/datasheets/rj45_12port.pdf>` | `Digi-Key <https://www.digikey.com/products/en?keywords=5569263>`_
2 | 40-pin WBUS Connector | :download:`DF40HC(4.0)-40DS-0.4V(70)<../../manufacturing/datasheets/40_pin_connector.pdf>` | `Digi-Key <https://www.digikey.com/product-detail/en/DF40HC(4.0)-40DS-0.4V(70)/H124604CT-ND/5155907/?itemSeq=290724516>`_
1 | Micro USB horizontal socket | :download:`10118194-0001LF<../../manufacturing/datasheets/horz_µUSB.pdf>` | `Digi-Key <https://www.digikey.com/products/en?keywords=609-4618-1-ND>`_
1 | 5V DC to DC Converter | :download:`R-78E5.0-1.0<../../manufacturing/datasheets/dc_converter.pdf>` | `Digi-Key <https://www.digikey.com/products/en?keywords=945-2201-ND>`_
3 | Transistor Array | :download:`TBD62083AFNG<../../manufacturing/datasheets/transistor_array.pdf>` | `Digi-Key <https://www.digikey.com/product-detail/en/toshiba-semiconductor-and-storage/TBD62083AFNGEL/TBD62083AFNGELCT-ND/5514123>`_
1 | Diode | :download:`MBR120VLSFT3G<../../manufacturing/datasheets/diode.pdf>` | `Digi-Key <https://www.digikey.com/product-detail/en/on-semiconductor/MBR120VLSFT3G/MBR120VLSFT3GOSCT-ND/3487322>`_

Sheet: pyboardbreakout_data
Qty | Description | Manufacturer P/N | Datasheet Filename | Vendor Name | Link
1 | Printed Circuit Board | pyControl D-Series Breakout 1.4 | breakout.pdf | OSH Park | https://oshpark.com/shared_projects/qB3NMaHN (https://oshpark.com/shared_projects/x12GQ4xq)
1 | Large Button | TL3300DF160Q | tactile_switch_large.pdf | Digi-Key | https://www.digikey.com/products/en?keywords=EG4906CT-ND
1 | Small Button | B3FS-1010P | tactile_switch_small.pdf | Digi-Key | https://www.digikey.com/products/en?keywords=sw1440ct
1 | Barrel Jack Connector | PJ-037A | barrel_jack.pdf | Digi-Key | https://www.digikey.com/products/en?keywords=CP-037A-ND
2 | 12-Port RJ45 Connector | 5569263-1 | rj45_12port.pdf | Digi-Key | https://www.digikey.com/products/en?keywords=5569263
2 | 40-pin WBUS Connector | DF40HC(4.0)-40DS-0.4V(70) | 40_pin_connector.pdf | Digi-Key | https://www.digikey.com/product-detail/en/DF40HC(4.0)-40DS-0.4V(70)/H124604CT-ND/5155907/?itemSeq=290724516
1 | Micro USB horizontal socket | 10118194-0001LF | horz_µUSB.pdf | Digi-Key | https://www.digikey.com/products/en?keywords=609-4618-1-ND
1 | 5V DC to DC Converter | R-78E5.0-1.0 | dc_converter.pdf | Digi-Key | https://www.digikey.com/products/en?keywords=945-2201-ND (https://www.digikey.com/product-detail/en/on-semiconductor/MC7805BDTRKG/MC7805BDTRKGOSCT-ND/1139742)
3 | Transistor Array | TBD62083AFNG | transistor_array.pdf | Digi-Key | https://www.digikey.com/product-detail/en/toshiba-semiconductor-and-storage/TBD62083AFNGEL/TBD62083AFNGELCT-ND/5514123
1 | Diode | MBR120VLSFT3G | diode.pdf | Digi-Key | https://www.digikey.com/product-detail/en/on-semiconductor/MBR120VLSFT3G/MBR120VLSFT3GOSCT-ND/3487322

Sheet: other materials
Qty | Description | Order Link | Required | Text | link
1 | D-series Breakout Board | `Build your own <build_section_>`_ | Yes
1 | pyboard D-series Microcontroller | `Micropython <https://store.micropython.org/product/PYBD-SF6-W4F2>`_ | Yes | Micropython | https://store.micropython.org/product/PYBD-SF6-W4F2
1 | 12V DC Power Supply | `Digi-Key <https://www.digikey.com/products/en?keywords=102-3631-ND>`_ | Yes | Digi-Key | https://www.digikey.com/products/en?keywords=102-3631-ND
1 | USB cable | `Digi-Key <https://www.digikey.com/products/en?keywords=380-1431-ND>`_ | Yes | Digi-Key | https://www.digikey.com/products/en?keywords=380-1431-ND
1 | DIN Rail | `Digi-Key <https://www.digikey.com/short/prn3bb>`_ |  | Digi-Key | https://www.digikey.com/short/prn3bb
2 | DIN Rail Adapter | `Digi-Key <https://www.digikey.com/products/en?keywords=277-2296-nd>`_ |  | Digi-Key | https://www.digikey.com/products/en?keywords=277-2296-nd
4 | M3 screws | `Digi-Key <https://www.digikey.com/products/en?keywords=335-1156-ND>`_ |  | Digi-Key | https://www.digikey.com/products/en?keywords=335-1156-ND

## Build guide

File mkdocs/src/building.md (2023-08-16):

# Building

<a href="render_iso.png">
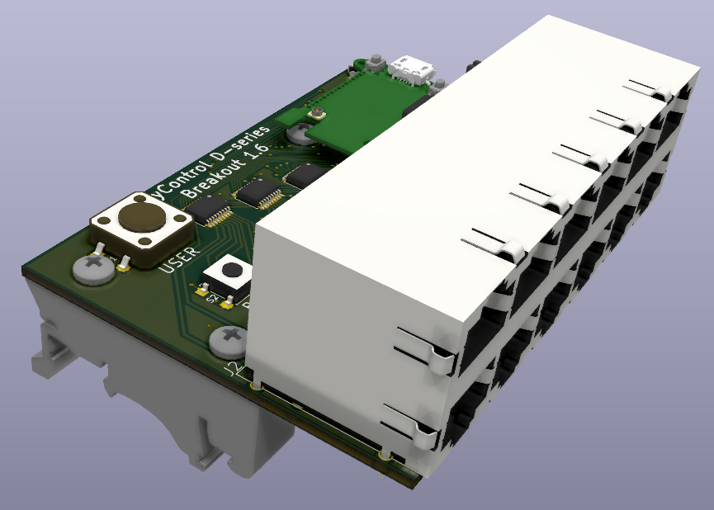
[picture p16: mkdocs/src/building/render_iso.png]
  
</a>
<a href="render_top.png">
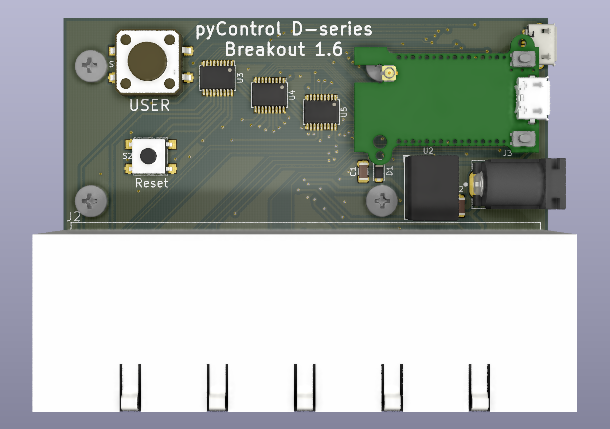
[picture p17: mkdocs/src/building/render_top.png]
  
</a>

## Printed Circuit Board

=== "layout"
    <a href="layout.png">
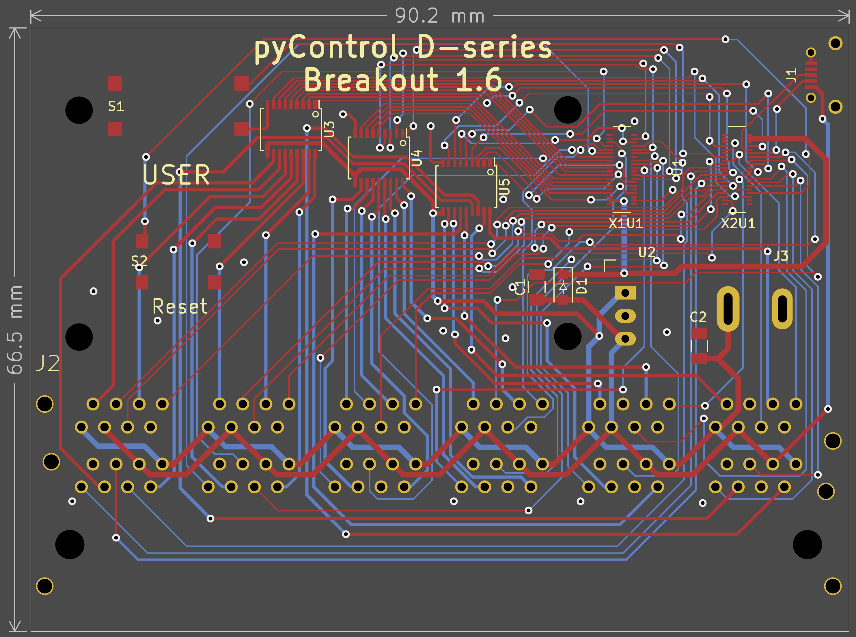
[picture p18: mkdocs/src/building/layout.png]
        
    </a>
=== "schematic"
    <a href="schematic.png">
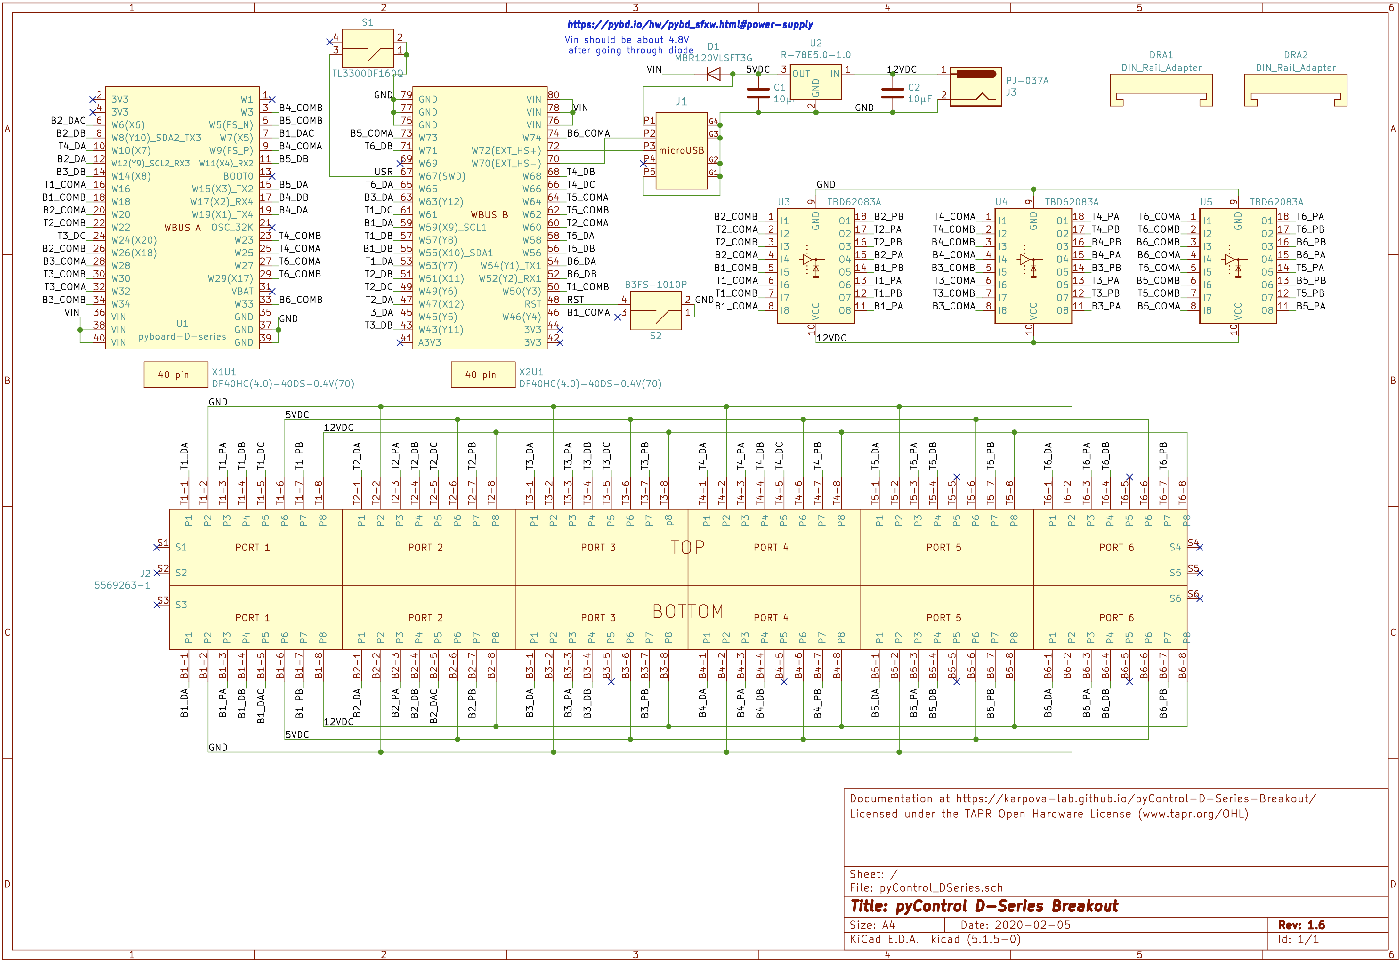
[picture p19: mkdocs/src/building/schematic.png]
        
    </a>

[:material-file-download: dseries_breakout_gerber.zip](building/dseries_breakout_gerber.zip)

[Order PCB from OSH Park](https://oshpark.com/shared_projects/lf2ETrxW)

## Bill of Materials

[View interactive BOM](building/pyControl_DSeries_1.6.html){ .md-button }

| Qty | Reference  | Description            | Value/MPN                                                                               | 
|-----|------------|------------------------|-----------------------------------------------------------------------------------------|
| 2   | C1, C2     | 1206 Capacitor         | [10µF](https://www.digikey.com/products/en?keywords=1276-1804-1-ND)                     | 
| 1   | D1         | Schottky Diode         | [MBR120VLSFT3G](https://www.digikey.com/products/en?keywords=MBR120VLSFT3GOSCT-ND)      | 
| 1   | J1         | Micro USB Socket       | [10118194-0001LF](https://www.digikey.com/products/en?keywords=609-4618-1-ND)           | 
| 1   | J2         | 12-port RJ45 Connector | [5569263-1](https://www.digikey.com/products/en?keywords=5569263)                       | 
| 1   | J3         | Barrel Jack Connector  | [PJ-037A](https://www.digikey.com/product-detail/en/cui-inc/PJ-037A/CP-037A-ND/1644545) | 
| 1   | S1         | Large Tactile Switch   | [TL3300DF160Q](https://www.digikey.com/products/en?keywords=EG4906CT-ND)                | 
| 1   | S2         | Small Tactile Switch   | [B3FS-1010P](https://www.digikey.com/products/en?keywords=sw1440ct)                     | 
| 1   | U2         | 5V DC to DC Converter  | [R-78E5.0-1.0](https://www.digikey.com/products/en?keywords=945-2201-ND)                | 
| 3   | U3, U4, U5 | 8-channel Driver Array | [TBD62083A](https://www.digikey.com/products/en?keywords=TBD62083AFNGELCT-ND)           | 
| 2   | X1U1, X2U1 | 40-pin Connector       | [DF40HC(4.0)-40DS-0.4V(70)](https://www.digikey.com/products/en?keywords=H124604CT-ND)  |

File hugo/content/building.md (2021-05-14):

# Building

{{< columns >}} <!-- begin columns block -->



<---> <!-- magic separator, between columns -->



{{< /columns >}}

## Printed Circuit Board
{{< columns >}}
Schematic:
<a href="schematic.png">
  
</a>
<--->
Layout:
<a href="render.png">
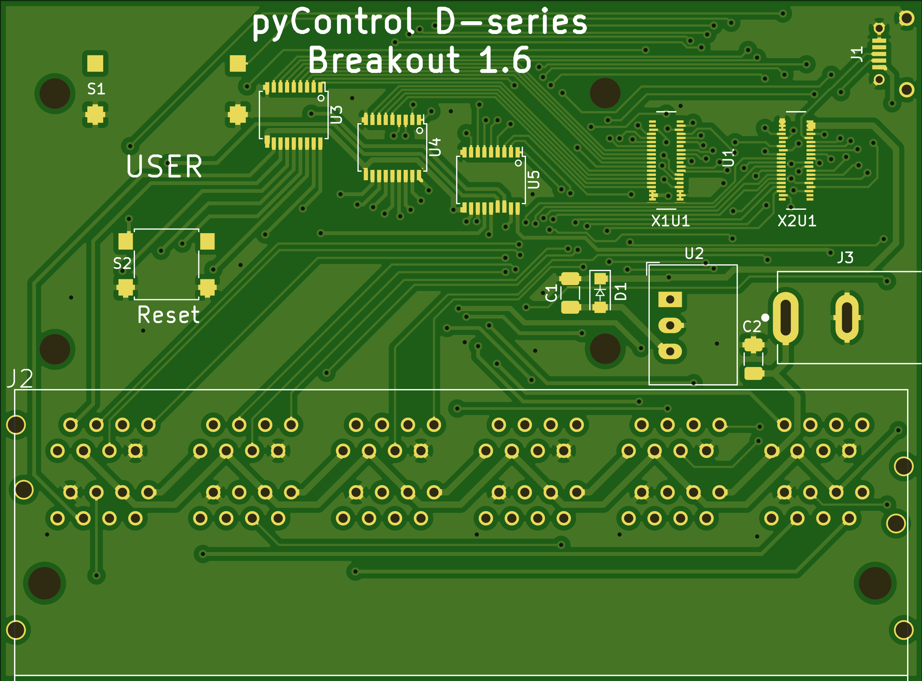
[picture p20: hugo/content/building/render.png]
  
</a>
{{< /columns >}}

{{< download filename="dseries_breakout_gerber.zip" text="dseries_breakout_gerber.zip" >}}
<br>

<a href="https://oshpark.com/shared_projects/lf2ETrxW">
    
</a>

## Bill of Materials

{{< button href="pyControl_DSeries_1.6.html" >}}View interactive BOM{{< /button >}}

| Qty | Reference  | Description            | Value/MPN                                                                               | 
|-----|------------|------------------------|-----------------------------------------------------------------------------------------|
| 2   | C1, C2     | 1206 Capacitor         | [10µF](https://www.digikey.com/products/en?keywords=1276-1804-1-ND)                     | 
| 1   | D1         | Schottky Diode         | [MBR120VLSFT3G](https://www.digikey.com/products/en?keywords=MBR120VLSFT3GOSCT-ND)      | 
| 1   | J1         | Micro USB Socket       | [10118194-0001LF](https://www.digikey.com/products/en?keywords=609-4618-1-ND)           | 
| 1   | J2         | 12-port RJ45 Connector | [5569263-1](https://www.digikey.com/products/en?keywords=5569263)                       | 
| 1   | J3         | Barrel Jack Connector  | [PJ-037A](https://www.digikey.com/product-detail/en/cui-inc/PJ-037A/CP-037A-ND/1644545) | 
| 1   | S1         | Large Tactile Switch   | [TL3300DF160Q](https://www.digikey.com/products/en?keywords=EG4906CT-ND)                | 
| 1   | S2         | Small Tactile Switch   | [B3FS-1010P](https://www.digikey.com/products/en?keywords=sw1440ct)                     | 
| 1   | U2         | 5V DC to DC Converter  | [R-78E5.0-1.0](https://www.digikey.com/products/en?keywords=945-2201-ND)                | 
| 3   | U3, U4, U5 | 8-channel Driver Array | [TBD62083A](https://www.digikey.com/products/en?keywords=TBD62083AFNGELCT-ND)           | 
| 2   | X1U1, X2U1 | 40-pin Connector       | [DF40HC(4.0)-40DS-0.4V(70)](https://www.digikey.com/products/en?keywords=H124604CT-ND)  | 

{{< previous link="./" text="Overview" >}}
{{< next link="using" text="Using" >}}

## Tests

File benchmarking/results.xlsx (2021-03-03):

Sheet: latency
 | MCU | Test | Sample | frequency (MHz) | Micropython Version | mean | std | min | max | fraction < 2ms | fraction < 1ms | Notes | port | Input pin | output pin
No Load | pyboard | 1 | 1 | 168 | 1.9.3 | 630.1 | 15.3 | 596 | 672 | 1.0000 | 1.0000 |  | 1 | x1 | x2
 |  | 1 | 2 | 168 | 1.9.3 | 630.1 | 15.1 | 596 | 672 | 1.0000 | 1.0000 | confirmed that changing pin doesn't make a difference | 5 | y5 | y6
 |  | 1 | 3 | 168 | 1.13 | 560.8 | 15.5 | 530 | 598 | 1.0000 | 1.0000 | upgrading firmware gives large improvement. Now getting comparable results to those reported in manuscript | 1 | x1 | x2
 | dseries | 2 | 1 | 144 | 1.11 | 466.7 | 12.5 | 438 | 502 | 1.0000 | 1.0000 |  | 6 | w50 | w46
 |  | 2 | 2 | 144 | 1.11 | 466.3 | 12.6 | 438 | 500 | 1.0000 | 1.0000 | confirming that identical conditions (2-1 and 2-2) give similar results | 6 | w50 | w46
 |  | 2 | 3 | 216 | 1.11 | 320.3 | 9 | 288 | 332 | 1.0000 | 1.0000 | increasing clock speed gives an improvement as expected | 6 | w50 | w46
 |  | 2 | 4 | 216 | 1.13 | 306.9 | 8.5 | 302 | 350 | 1.0000 | 1.0000 | latest firmware and highest clock speed gives best results | 6 | w50 | w46
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

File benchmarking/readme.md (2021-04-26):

This folder contains the files needed to analyze the performance of the [pyControl D-series Breakout](https://karpova-lab.github.io/pyControl-D-Series-Breakout/) in comparison to the official [pyControl Breakout 1.2](https://pycontrol.readthedocs.io/en/latest/user-guide/hardware/#breakout-board-12). 

Data was collected from both pyboards ([v1.1](https://store.micropython.org/product/PYBv1.1#_) and [D-Series SF6W](https://store.micropython.org/product/PYBD-SF6-W4F2)) using an [Analog Discovery 2](https://reference.digilentinc.com/reference/instrumentation/analog-discovery-2/start) oscilloscope.

To repeat the analysis use the [timing_analysis_ipynb](https://github.com/Karpova-Lab/pyControl-D-Series-Breakout/blob/master/benchmarking/timing_analysis.ipynb). The .npy data files can be downloaded from Dropbox [here](https://www.dropbox.com/sh/ct0zpvxmnmsktt1/AABsgd3lGLtRtKHfQOnN4Qg-a?dl=0).

The comparison was made by repeating the same methods found in [pyControl: Open source, Python based, hardware and software for controlling behavioural neuroscience experiments](https://www.biorxiv.org/content/10.1101/2021.02.22.432227v1). Below are excerpts from the manuscript describing the methods.

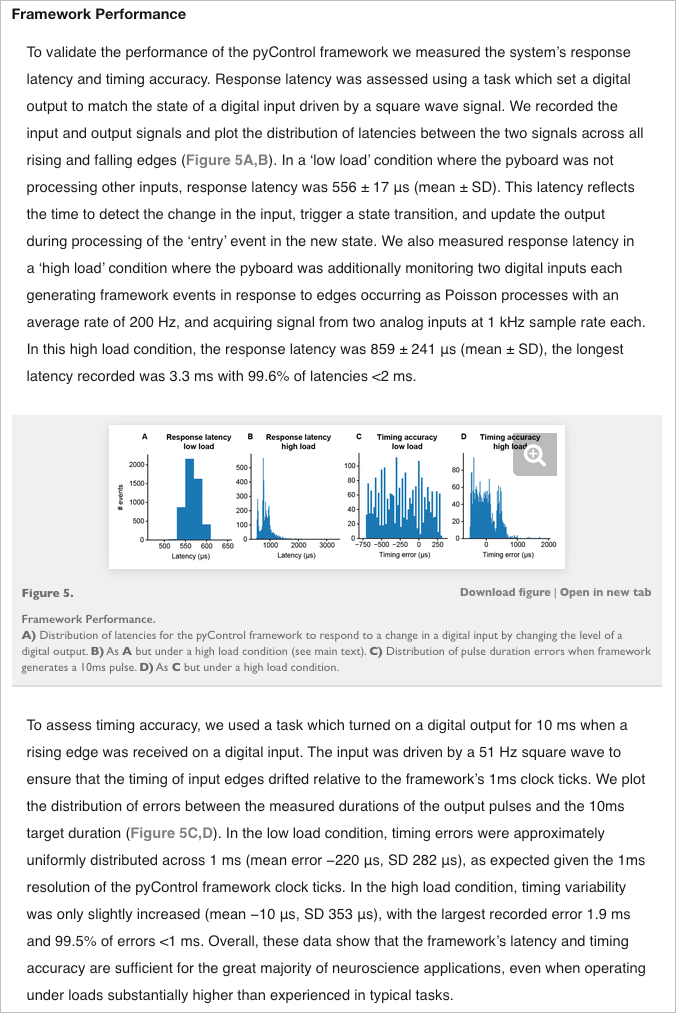
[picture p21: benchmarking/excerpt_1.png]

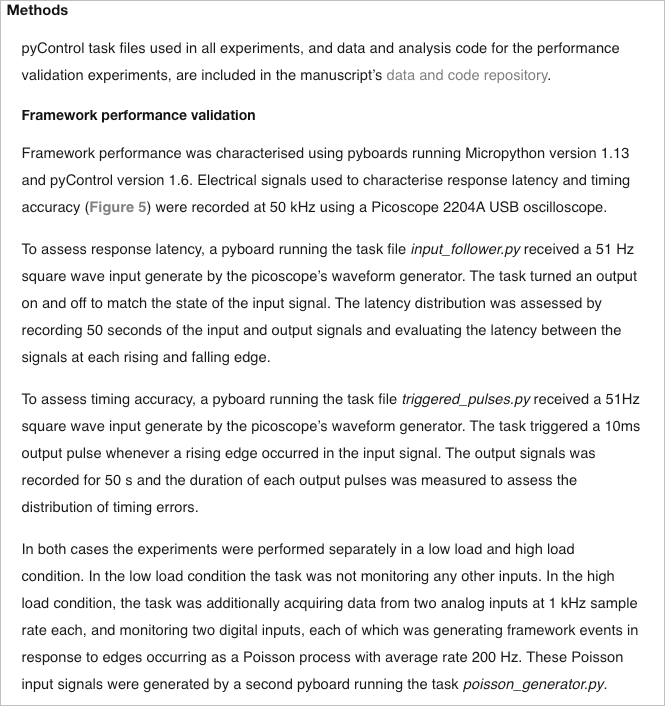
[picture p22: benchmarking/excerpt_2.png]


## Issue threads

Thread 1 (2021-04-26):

### ISSUE TITLE
Wrong Pinout

### ISSUE THREAD

**Issue by AtMostafa** [Karpova-Lab/pyControl-D-Series-Breakout#1]
Hello,

I managed to run the SPI2 port after days of struggle. The issue was the mistake in the pinout of Port2 DIO_B which based on the spreadsheet is the clock line, but it's not.
I noticed that DIO_B and C have been swapped on the website since I printed down my copy, but I think it is still wrong in the spreadsheet.

**Comment by alustig3** [comment]
The spreadsheet has been corrected in aca1b7563fcda5f1fbce0720579d3f11688c5208

Sorry the mistake caused you trouble. Thanks so much for reporting the issue!

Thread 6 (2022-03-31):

### ISSUE TITLE
SPI chip select

### ISSUE THREAD

**Issue by AtMostafa** [Karpova-Lab/pyControl-D-Series-Breakout#6]
In micropython version 1.18 (and possibly earlier versions), the Chip Select (or SS) line of the hardware SPI is configurable by the user, from [docs](https://docs.micropython.org/en/v1.9.3/wipy/library/machine.SPI.html):
> Management of an SS signal should happen in user code (via machine.Pin class)

So multiple devices can easily share only one SPI bus and have their own CS, [here](https://github.com/BeNeuroLab/PyTreadmillTask/blob/a54120618892bfddf0d39d9f1b2b57f999ccef32/devices/_PMW3360DM.py#L343) is an example of 2 mouse sensors sharing SPI2.

Pretty minor, but I think it's nicer to update the SPI table on the website ([here](https://github.com/Karpova-Lab/pyControl-D-Series-Breakout/blob/7e3bf519f14bf59fba8e6f6569546ace7d7827d5/mkdocs/src/using.md?plain=1#L54)) so people don't think they are restricted to the specified CS pin :)

Bests,

**Comment by alustig3** [comment]
Ah yes you're absolutely right. Thanks so much for pointing that out!

fixed in 999bcb788e3a692fdda5ce456eb1d312666dd67d

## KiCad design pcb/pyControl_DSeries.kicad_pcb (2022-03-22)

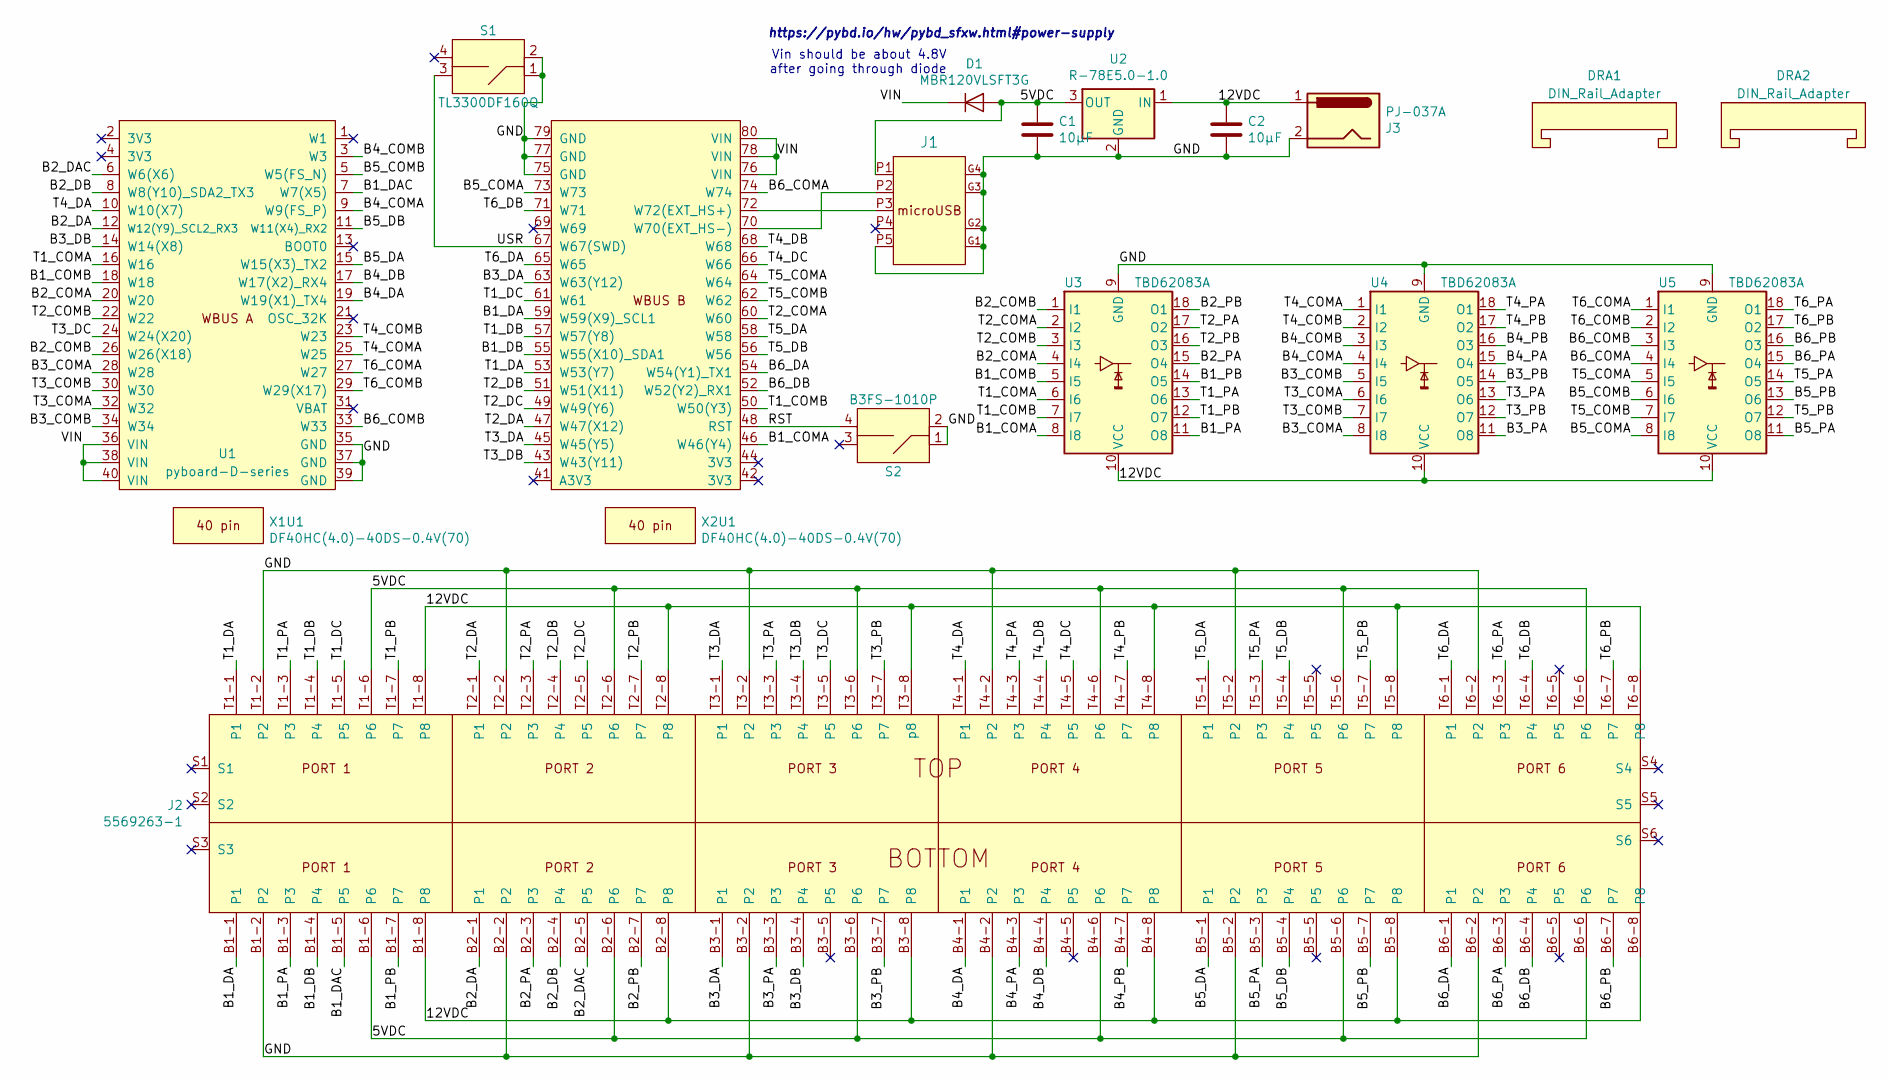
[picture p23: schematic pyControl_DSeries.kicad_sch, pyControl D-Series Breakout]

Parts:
C1, C2: 10µF; C_1206_3216Metric
D1: MBR120VLSFT3G; D_SOD-123F
DRA1, DRA2: DIN_Rail_Adapter; DIN_Clip
J1: 10118194-0001LF; microUSB_horizontal_socket
J2: 5569263-1; RJ45_12Port
J3: PJ-037A; DC_Jack
S1: TL3300DF160Q; 12mm_tactile_smd
S2: B3FS-1010P; 6mm_tactile_smd
U1: pyboard-D-series; PyBoard_D-Series
U2: R-78E5.0-1.0; Converter_DCDC_RECOM_R-78E-0.5_THT
U3, U4, U5: TBD62083A; SSOP-18_4.4x6.5mm_P0.65mm
X1U1, X2U1: DF40HC(4.0)-40DS-0.4V(70); Hirose_40_pin

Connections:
/5VDC: C1.1, D1.2 (A), J1.P1, J2.B1-6 (P6), J2.B2-6 (P6), J2.B3-6 (P6), J2.B4-6 (P6), J2.B5-6 (P6), J2.B6-6 (P6), J2.T1-6 (P6), J2.T2-6 (P6), J2.T3-6 (P6), J2.T4-6 (P6), J2.T5-6 (P6), J2.T6-6 (P6), U2.3 (OUT)
/12VDC: C2.1, J2.B1-8 (P8), J2.B2-8 (P8), J2.B3-8 (P8), J2.B4-8 (P8), J2.B5-8 (P8), J2.B6-8 (P8), J2.T1-8 (P8), J2.T2-8 (P8), J2.T3-8 (p8), J2.T4-8 (P8), J2.T5-8 (P8), J2.T6-8 (P8), J3.1, U2.1 (IN), U3.10 (VCC), U4.10 (VCC), U5.10 (VCC)
/B1_COMA: U1.46 (W46(Y4)), U3.8 (I8)
/B1_COMB: U1.18 (W18), U3.5 (I5)
/B1_DA: J2.B1-1 (P1), U1.59 (W59(X9)_SCL1)
/B1_DAC: J2.B1-5 (P5), U1.7 (W7(X5))
/B1_DB: J2.B1-4 (P4), U1.55 (W55(X10)_SDA1)
/B1_PA: J2.B1-3 (P3), U3.11 (O8)
/B1_PB: J2.B1-7 (P7), U3.14 (O5)
/B2_COMA: U1.20 (W20), U3.4 (I4)
/B2_COMB: U1.26 (W26(X18)), U3.1 (I1)
/B2_DA: J2.B2-1 (P1), U1.12 (W12(Y9)_SCL2_RX3)
/B2_DAC: J2.B2-5 (P5), U1.6 (W6(X6))
/B2_DB: J2.B2-4 (P4), U1.8 (W8(Y10)_SDA2_TX3)
/B2_PA: J2.B2-3 (P3), U3.15 (O4)
/B2_PB: J2.B2-7 (P7), U3.18 (O1)
/B3_COMA: U1.28 (W28), U4.8 (I8)
/B3_COMB: U1.34 (W34), U4.5 (I5)
/B3_DA: J2.B3-1 (P1), U1.63 (W63(Y12))
/B3_DB: J2.B3-4 (P4), U1.14 (W14(X8))
/B3_PA: J2.B3-3 (P3), U4.11 (O8)
/B3_PB: J2.B3-7 (P7), U4.14 (O5)
/B4_COMA: U1.9 (W9(FS_P)), U4.4 (I4)
/B4_COMB: U1.3 (W3), U4.3 (I3)
/B4_DA: J2.B4-1 (P1), U1.19 (W19(X1)_TX4)
/B4_DB: J2.B4-4 (P4), U1.17 (W17(X2)_RX4)
/B4_PA: J2.B4-3 (P3), U4.15 (O4)
/B4_PB: J2.B4-7 (P7), U4.16 (O3)
/B5_COMA: U1.73 (W73), U5.8 (I8)
/B5_COMB: U1.5 (W5(FS_N)), U5.6 (I6)
/B5_DA: J2.B5-1 (P1), U1.15 (W15(X3)_TX2)
/B5_DB: J2.B5-4 (P4), U1.11 (W11(X4)_RX2)
/B5_PA: J2.B5-3 (P3), U5.11 (O8)
/B5_PB: J2.B5-7 (P7), U5.13 (O6)
/B6_COMA: U1.74 (W74), U5.4 (I4)
/B6_COMB: U1.33 (W33), U5.3 (I3)
/B6_DA: J2.B6-1 (P1), U1.54 (W54(Y1)_TX1)
/B6_DB: J2.B6-4 (P4), U1.52 (W52(Y2)_RX1)
/B6_PA: J2.B6-3 (P3), U5.15 (O4)
/B6_PB: J2.B6-7 (P7), U5.16 (O3)
/GND: C1.2, C2.2, J1.G1, J1.G2, J1.G3, J1.G4, J1.P5, J2.B1-2 (P2), J2.B2-2 (P2), J2.B3-2 (P2), J2.B4-2 (P2), J2.B5-2 (P2), J2.B6-2 (P2), J2.T1-2 (P2), J2.T2-2 (P2), J2.T3-2 (P2), J2.T4-2 (P2), J2.T5-2 (P2), J2.T6-2 (P2), J3.2, S1.1 (in1), S1.2 (in2), S2.1 (in1), S2.2 (in2), U1.35 (GND), U1.37 (GND), U1.39 (GND), U1.75 (GND), U1.77 (GND), U1.79 (GND), U2.2 (GND), U3.9 (GND), U4.9 (GND), U5.9 (GND)
/RST: S2.4 (out2), U1.48 (RST)
/T1_COMA: U1.16 (W16), U3.6 (I6)
/T1_COMB: U1.50 (W50(Y3)), U3.7 (I7)
/T1_DA: J2.T1-1 (P1), U1.53 (W53(Y7))
/T1_DB: J2.T1-4 (P4), U1.57 (W57(Y8))
/T1_DC: J2.T1-5 (P5), U1.61 (W61)
/T1_PA: J2.T1-3 (P3), U3.13 (O6)
/T1_PB: J2.T1-7 (P7), U3.12 (O7)
/T2_COMA: U1.60 (W60), U3.2 (I2)
/T2_COMB: U1.22 (W22), U3.3 (I3)
/T2_DA: J2.T2-1 (P1), U1.47 (W47(X12))
/T2_DB: J2.T2-4 (P4), U1.51 (W51(X11))
/T2_DC: J2.T2-5 (P5), U1.49 (W49(Y6))
/T2_PA: J2.T2-3 (P3), U3.17 (O2)
/T2_PB: J2.T2-7 (P7), U3.16 (O3)
/T3_COMA: U1.32 (W32), U4.6 (I6)
/T3_COMB: U1.30 (W30), U4.7 (I7)
/T3_DA: J2.T3-1 (P1), U1.45 (W45(Y5))
/T3_DB: J2.T3-4 (P4), U1.43 (W43(Y11))
/T3_DC: J2.T3-5 (P5), U1.24 (W24(X20))
/T3_PA: J2.T3-3 (P3), U4.13 (O6)
/T3_PB: J2.T3-7 (P7), U4.12 (O7)
/T4_COMA: U1.25 (W25), U4.1 (I1)
/T4_COMB: U1.23 (W23), U4.2 (I2)
/T4_DA: J2.T4-1 (P1), U1.10 (W10(X7))
/T4_DB: J2.T4-4 (P4), U1.68 (W68)
/T4_DC: J2.T4-5 (P5), U1.66 (W66)
/T4_PA: J2.T4-3 (P3), U4.18 (O1)
/T4_PB: J2.T4-7 (P7), U4.17 (O2)
/T5_COMA: U1.64 (W64), U5.5 (I5)
/T5_COMB: U1.62 (W62), U5.7 (I7)
/T5_DA: J2.T5-1 (P1), U1.58 (W58)
/T5_DB: J2.T5-4 (P4), U1.56 (W56)
/T5_PA: J2.T5-3 (P3), U5.14 (O5)
/T5_PB: J2.T5-7 (P7), U5.12 (O7)
/T6_COMA: U1.27 (W27), U5.1 (I1)
/T6_COMB: U1.29 (W29(X17)), U5.2 (I2)
/T6_DA: J2.T6-1 (P1), U1.65 (W65)
/T6_DB: J2.T6-4 (P4), U1.71 (W71)
/T6_PA: J2.T6-3 (P3), U5.18 (O1)
/T6_PB: J2.T6-7 (P7), U5.17 (O2)
/USR: S1.3 (out1), U1.67 (W67(SWD))
/VIN: D1.1 (K), U1.36 (VIN), U1.38 (VIN), U1.40 (VIN), U1.76 (VIN), U1.78 (VIN), U1.80 (VIN)
unnamed: J1.P2, U1.70 (W70(EXT_HS-))
unnamed: J1.P3, U1.72 (W72(EXT_HS+))

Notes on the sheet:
https://pybd.io/hw/pybd_sfxw.html#power-supply
Vin should be about 4.8V after going through diode

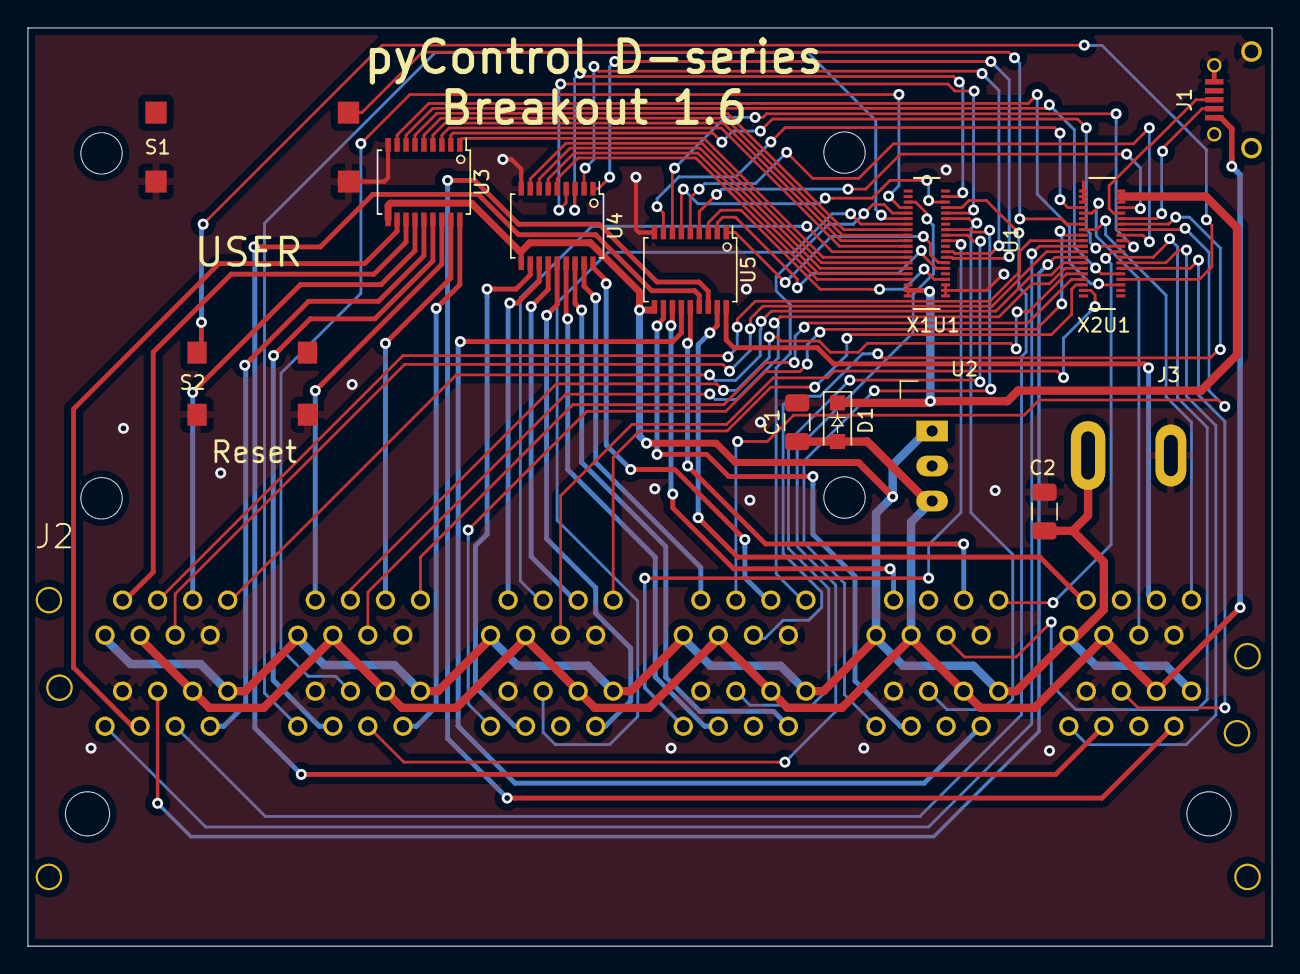
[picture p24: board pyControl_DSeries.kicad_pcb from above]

Board: 2 copper layers, 90.2 x 66.5 mm, 17 parts (0 on the bottom side), 86 nets.

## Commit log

2019-04-12 Initial commit. v1.0
    [pyControl_DSeries-B_Cu.gbr, pyControl_DSeries-B_Mask.gbr, pyControl_DSeries-B_Paste.gbr, pyControl_DSeries-B_SilkS.gbr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]
2019-04-24 rev 1.1 fixed pins on dc jack and linear regulator. connected T3_DC repositioned DIN adapters added BOM and datasheets
    [BOM.xlsx, pyControl_DSeries-B_Cu.gbr, pyControl_DSeries-B_Mask.gbr, pyControl_DSeries-B_Paste.gbr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]
2019-05-07 made footprint and symbol libraries local to project
    [pyControl_DSeries.kicad_pcb]
2019-05-07 rough draft of documentation added
    [BOM.xlsx]
2019-05-09 pcb libraries are now a git submodule
    [pyControl_DSeries.kicad_pcb]
2019-05-09 Revised PCB to v1.2 Switched from linear regulator to DC-DC converter. 1µF capacitors are now 10µF. Added TAPR link to silkscreen and schematic.
    [BOM.xlsx, pyControl_DSeries.kicad_pcb]
2019-05-13 Doc update
    [BOM.xlsx]
2019-07-26 pcb version 1.3. W1 cannot be used as DIO, so now B4_COMA is connected to pin9 (W9). W69 cannot be used as DIO, so now B5_COMB is connected to pin5 (W5). Added microusb connector so that you can perm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
    [BOM.xlsx, pyControl_DSeries.kicad_pcb, pyControl_DSeries.sch]
2019-07-26 updated docs for v1.3
    [BOM.xlsx]
2019-07-26 micro usb socket was missing from docs
    [BOM.xlsx]
2019-07-29 Doc update. Added more resource links. Comparison now uses highest tier d-series board PYBD-SF6-W4F2
2019-08-05 PCB rev 1.4 removed mounting pads from D40 Hirose connector since that version of connector is discontinued. shifted pyboard connectors down and to the left so now an SD card can be inserted without 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
    [BOM.xlsx, pyControl_DSeries.kicad_pcb, pyControl_DSeries.sch]
2019-10-17 pcb v1.5. Rearranged pins to jack mapping.
    To get top row inputs on separate interrupt vectors
    T3_C was W74, now Q24
    T4_B was W62, now W68
    T4_C was W60, now W66
    T6_A was W50, now W65
    T6_A was W46, now W71
    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
    [bom.xlsx, pyControl_DSeries.kicad_pcb, pyControl_DSeries.sch]
2019-10-29 updated device file
2020-04-02 pcb v1.6. new rj45 footprint. swapped W49 and W51 so now interrupt vector 13 is on DIO_C of port 2. can have entire row of DIO-A and DIO-B interrupts without collisions
    [bom.xlsx, pyControl_DSeries.kicad_pcb]
2021-03-02 Doc update
    - added notes about SPI and interrupt vectors
    - fixed pinout diagram. Port 2 DIO_B and DIO_C were swapped.
    [spi_ports.xlsx]
2021-03-03 Added benchmarking data and analysis
    [results.xlsx]
2021-04-26 Fixed SPI port spreadsheet and other doc cleanup
    A mistake in the pinout diagram was corrected in commit bf2bec864f299681884a0b370ce6527de034c568 however the SPI port spreadsheet did not reflect the change.
    spreadsheet updates:
    - SCK for SPI(2) was Port2B, now corrected to Port2C
    - fixed broken link to D-series pinouts.jpg
    other updates:
    - added labeled diagram to overview page
    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
    [spi_ports.xlsx]
2021-05-14 Change from sphinx docs to Hugo docs
    [spi_ports.xlsx]
2021-05-28 doc theme update
    [spi_ports.xlsx]
2022-03-22 update PCB files to KiCad v6
    [pyControl_DSeries.kicad_pcb, pyControl_DSeries.kicad_sch, pyControl_DSeries.sch]
2022-03-22 migrated docs from hugo to mkdocs
    [spi_ports.xlsx]

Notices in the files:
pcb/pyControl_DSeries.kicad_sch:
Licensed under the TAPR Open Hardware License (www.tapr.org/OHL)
